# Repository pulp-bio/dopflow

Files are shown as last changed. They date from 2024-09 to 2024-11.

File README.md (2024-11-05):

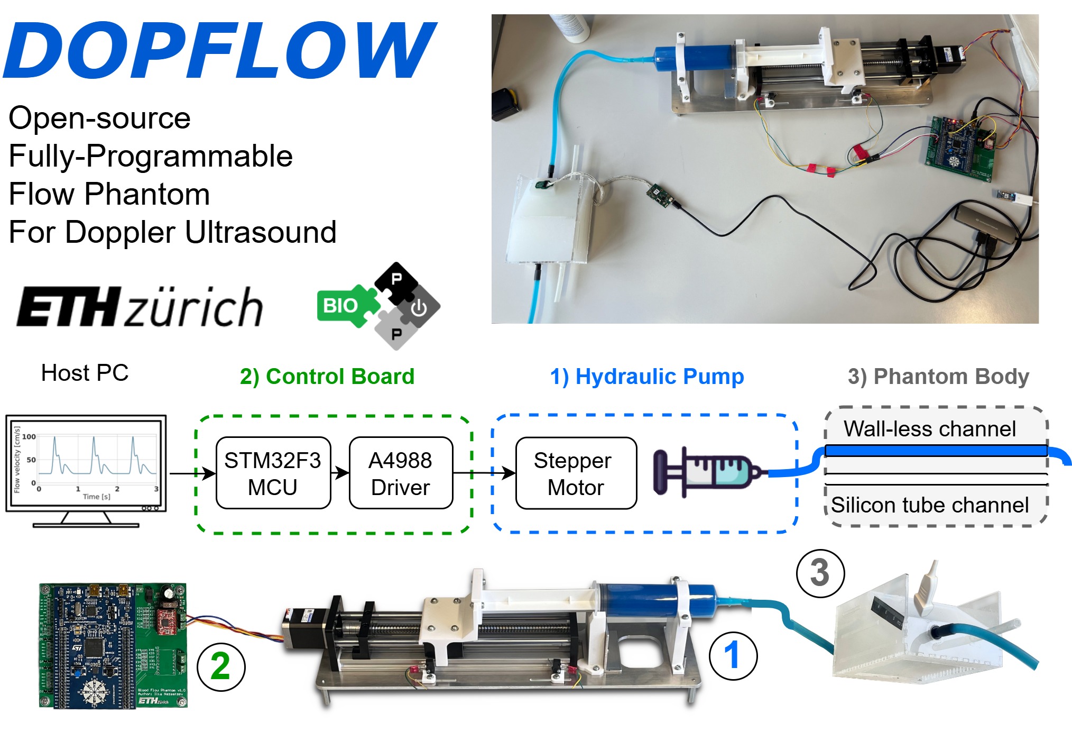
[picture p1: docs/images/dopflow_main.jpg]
DOPFLOW main


# DOPFLOW: 
## Open-Source Fully-Programmable Flow Phantom for Doppler Ultrasound
# Introduction

This repository contains the design files to reproduce the DOPFLOW system presented at IUS Joint Symposium 2024 [1].

DOPFLOW is an all-in-one Doppler Flow Phantom system that mimics the common carotid artery.
The platform has a modular design using off-the-shelf parts, including
- Custom syringe-based hydraulic pump, 
- Control printed circuit board, 
- Phantom body with both walled and wall-less channels,
- Graphical User Interface. 

The platform allows users to define pulsatile patterns, achieves maximum flow speeds over 1 meter per second and was validated with a commercial ultrasound Doppler machine (SONIX RP). These capabilities, plus the system's low cost (< 300 $) and open-source design, make DOPFLOW a promising research tool for developing new Doppler ultrasound technologies.

# Structure of the repository
This repository has the following folders:
- `control_board`, containing the source files to reproduce the control board.
- `hydraulic pump`, containing the source files to reproduce the hydraulic pump.
- `phantom`, containing the source files to reproduce the phantom structure, mimicking the common carotid artery and surrounding tissue.
- `software`, containing the source files for the graphical user interface (GUI) to control the motor.
- `docs`, containing the project documentation (e.g., images of the device, user manual, ...)

# Documentation 

The comprehensive [DOPFLOW User Manual](docs/dopflow_user_manual.pdf) located in the `docs/` folder, provides complete information on the DOPFLOW system, from assembly instructions to a detailed GUI overview. It’s designed to make the platform accessible and user-friendly for all, regardless of technical background.

# How to reproduce?

In a nutshell, to set up your own instance of DOPFLOW, follow these steps:

1. *Fabricate and assemble the hardware*<br>
   First, fabricate the phantom body and the hydraulic pump, then assemble and program the control board using instructions from the chapter 2 of the  [User Manual](docs/dopflow_user_manual.pdf) 

2. *Python dependencies installation on the host PC*<br>
   Follow the instructions in the `./software/` folder to install the dependencies.

# Usage

Please refer to chapter 3 of the [DOPFLOW User Manual](docs/dopflow_user_manual.pdf) for detailed information.

1. *Connect and power the control board*<br>
   Connect the PC to the control board, attach the hydraulic pump to the control board (connecting both the motor and limit switches), and power the control board using a 12 V, 2A lab power supply.

2. *Connect the phantom to the hydraulic pump*<br>
   Use a silicone hydraulic line to connect the phantom to the syringe pump.

3. *Run the graphical user interface (GUI)*<br>
   Launch the GUI, and use the controls to move the syringe and fill the phantom with the blood-mimicking fluid.

4. *Place the ultrasound transducer and perform measurements*<br>
   Position the ultrasound transducer on the phantom, run the custom pulse profile, and proceed with the measurements.

# Citation

[1] - Vostrikov Sergei et. al, "Open-Source Fully-Programmable Flow Phantom for Doppler Ultrasound." 2024 IEEE Ultrasonics, Ferroelectrics, and Frequency Control Joint Symposium (UFFC-JS). IEEE, 2024.

If you would like to reference the project, please cite the following paper:

```
@inproceedings{vostrikov2022opensource,
  title={Open-Source Fully-Programmable Flow Phantom for Doppler Ultrasound},
  author={Vostrikov, Sergei and Tille, Josquin and Nazemtsev, Ilia and Benini, Luca and Cossettini, Andrea},
  booktitle={2024 IEEE Ultrasonics, Ferroelectrics, and Frequency Control Joint Symposium (UFFC-JS)},
  pages={1--4},
  year={2024},
  organization={IEEE}
}
```

# Authors

The DOPFLOW system was developed at the [Integrated Systems Laboratory (IIS)](https://iis.ee.ethz.ch/) at ETH Zurich by:
- [Sergei Vostrikov](https://scholar.google.com/citations?user=a0KNUooAAAAJ&hl=en) (System design, Technical Supervision, Open-Sourcing)
- [Josquin Tille](https://www.linkedin.com/in/josquin-tille-829a341a7/) (Mechanical/PCB/Software design of the final prototype)
- [Nazemtsev Ilia](https://www.linkedin.com/in/ilia-nazemtsev/) (Mechanical/PCB/Software design of the initial prototype, Materials/Components selection)
- [Luca Benini](https://scholar.google.com/citations?hl=en&user=8riq3sYAAAAJ) (Supervision, Conceptualization)
- [Andrea Cossettini](https://scholar.google.com/citations?user=d8O91jIAAAAJ&hl=en) (Supervision, Project administration)

# License
Please see the [LICENSE_README.md](./LICENSE_README.md) for a summary of license information.

## Limitation of Liability
In no event and under no legal theory, whether in tort (including negligence), contract, or otherwise, unless required by applicable law (such as deliberate and grossly negligent acts) or agreed to in writing, shall any Contributor be liable to You for damages, including any direct, indirect, special, incidental, or consequential damages of any character arising as a result of this License or out of the use or inability to use the Work (including but not limited to damages for loss of goodwill, work stoppage, computer failure or malfunction, or any and all other commercial damages or losses), even if such Contributor has been advised of the possibility of such damages.

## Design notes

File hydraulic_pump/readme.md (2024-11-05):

# Assembly of the Hydraulic Pump
In this folder, you can find the files necessary to build the syringe based hydraulic pump.

For a step-by-step assembly instruction, please refer to the User manual located in `/docs/` folder and to the assembly video `assembly_animation.mp4` located in `/hydraulic_pump/`.

## Machined part
- `Ground_plate Drawing v4.pdf`, `Ground_plate.step`, are the plans to build the ground plate on which the component are mounted. It is made from a 5mm thick 500mm x 135mm aluminum plate. The pdf techincal drawing includes the specifications for the tolerances and threads

## 3D Printed parts
The 3D printed parts are printed with PLA using FDM printing
- `Barrel_holder_1.stl`, `Syringe_holder_2.stl` and `cap_1.stl` are the three element connecting the the syringe to the base plate
- `plunger_puller_4.stl` and `plunger_pusher_2.stl` are connecting the plunger to the CNC rail.

- `lim_sitch_holder_3.stl` needs to be printed 2x, once normaly and once **mirrored** along the xz plan

- `spacer_raiL1.stl` can be inserted between the end plate on the motor side of the CNC rail and the aluminum extrusion of the CNC rail if the motor's shaft is too long and extends into the ballscrew mechanism. 

## Off the shelf parts to order

Off the shelf parts have to be order online. More iformation about the products as well as links to the providers are found in the Bill of material: `pump_BOM.xlsx`
### Coupling CNC rail with step motor
The CNC motor comes with a coupling however it does not fit the step motor shaft's diamter. You should order a motor coupling with diameter 6mm and 8mm. 

## Assembly visual description
For assembly refer to the assembly video: https://youtu.be/GyMb5HX_3No.

The image below maps the names of the files to the components. 

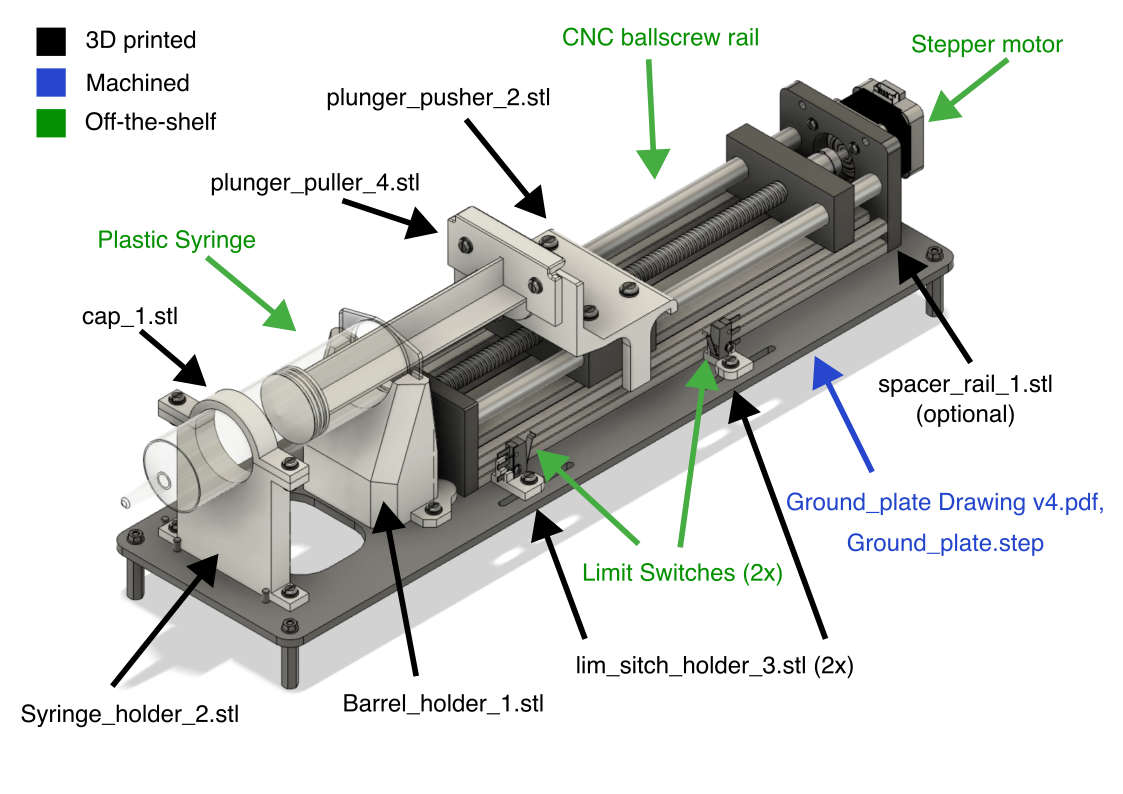
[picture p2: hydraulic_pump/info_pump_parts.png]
Hydraulic pump schematic


## Screws and Dowel pins 
Dowel pins for alignement: **ISO 2338 - ⌀4 h6 x 10mm** (7x)

Screws and washer:
- **Ground plate to CNC rail**: Stainless Steel Pan Head Slotted Screws **M6 x 15mm** + M6 washer (4x)
- **Plunger pusher to CNC rail**: Stainless Steel Pan Head Slotted Screws **M5 x 15mm** + M5 washer (4x)
- **Step motor to CNC rail**: Stainless Steel Pan Head Slotted Screws **M3 x 12mm** + M3 washer (4x)
- **Limit switch to lim stich holder**: Stainless Steel Pan Head Slotted Screws **M2 x 15mm** + M2 hex nut (2x) and M2 washer (4x)
- **All other Screws**: Stainless Steel Pan Head Slotted Screws **M4 x 15mm** + M4 hex nut (10x)  and M4 washer (20x)

- **4 support legs**: spacer, hex, M4 X 12mm

## Adjustment of the Limit Switches
The swithes can be mounted on the oblong holes on the side of the ground plate. To find the right position, 
- Start by mounting the Switches onto the holder. 
- Turn ballscrew mannualy until the syringe is almost empty (before the plunger touches the bottom of the barrel).
- Adjust the position of the holder so that the switch bumps into the plunger pusher and closes the circuit. 
- Turn ballscrew mannualy until the syringe is almost full (before the syringe breaks open).
- Adjust the position of the second holder so that the switch bumps into the plunger pusher and closes the circuit.

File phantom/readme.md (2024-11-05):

# Phantom's body fabrication

This directory contains the necessary instructions and files for fabricating a phantom body, including materials and steps for creating both walled and wall-less channels.

For a step-by-step manufacturing and assembly instructions, please refer to the User manual located in `/docs/` folder of the root directory of the repository.

## Summary of the Fabrication Steps

1. **Acrylic Frame Laser Cutting**
    - Laser cut the file `AcrilicBoxV4.svg` in acrylic and assemble the box using [acrifix glue](https://link-url-here.org).
    - Laser cut the `support_consturction_blocks.svg` using wither plywood or acrylic. 

2. **Prepare the Mold**
   - Insert a **silicone tube** (6 mm inner diameter) into pre-arranged holes in the frame. You can also add a metalic rod int the tube to ensure it will stay straight.
   - Place a **steel rod** (6 mm diameter) for the wall-less channel. TIP: coat the steel rod with petrolum jelly for easier removal
   - Seal all the open holes with transparent tape. You can print `phantom_hole_lid.stl`to cover the holes of the wall-less channel.
   - Place the frame onto the suport blocs

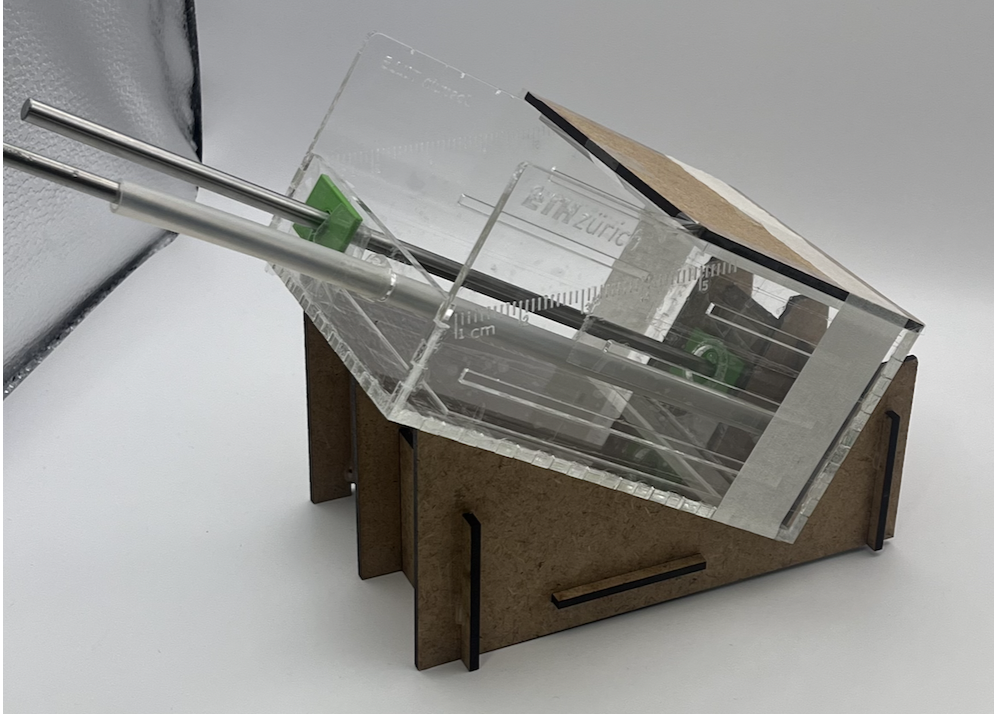
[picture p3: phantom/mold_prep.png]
Mold preparation


3. **Filling with Tissue-Mimicking Material**
   - Prepare a tissue-mimicking silicone rubber material (EcoFlex 30, Smooth-On, USA).
   - Mix part A and B with a 1:1 ratio.
   - Degas the EcoFlex silicone for **60 seconds** under a medium vacuum level (**15-20 mbar**) to remove any air bubbles.
   - After degassing, pour the silicone into the acrylic frame.
   - Allow the silicone to cure for **4 hours**.

4. **Removing the Sacrificial parts**
   - Once cured, carefully remove the steel rod from the phantom, leaving behind a **cylindrical wall-less channel**.
   - Remove all other sacrificial parts.
   - Insert the inlet to conect the wall-less channel to a conveyor silicon tube.

---

This process results in a phantom body with both walled and wall-less channels.
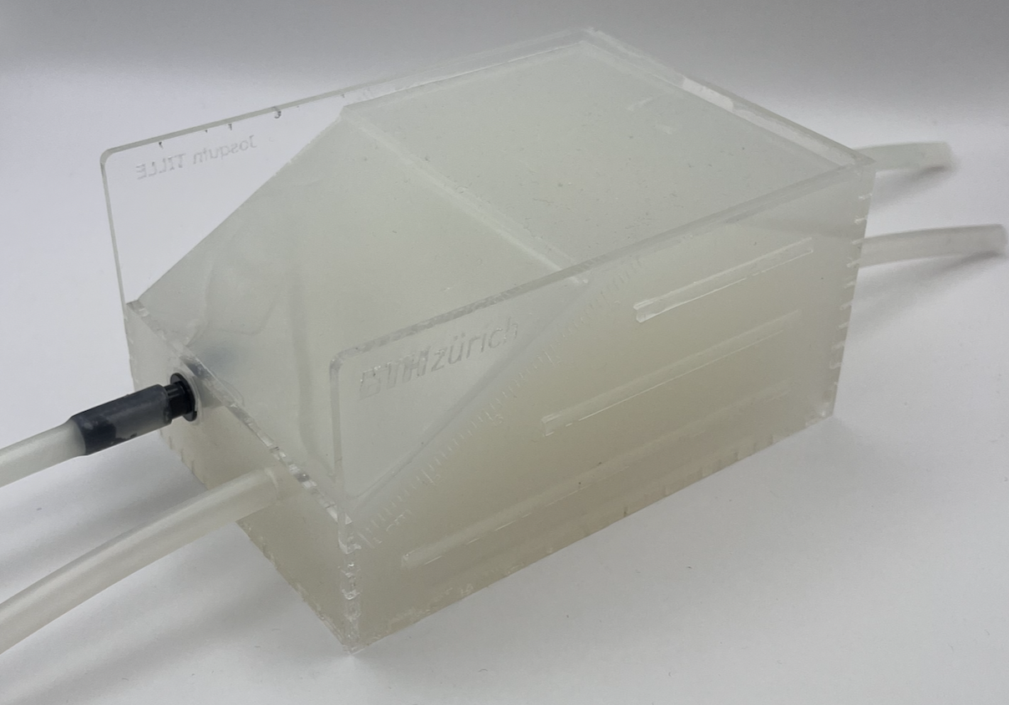
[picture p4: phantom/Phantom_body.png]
Mold final


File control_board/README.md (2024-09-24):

# Control board printed circuit board and firmware
This directory contains the following source files for the control board:
- Printed circuit board design files (`hw` folder)
- STM32 firmware (`fw` folder)

Please refer to the particular folder for license information.

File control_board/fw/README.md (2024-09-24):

# Flashing the firmware to the control board

### 1. Download STM32CubeIDE
Download and install the latest version **1.12.1** of STM32CubeIDE from the [ ST website](https://www.st.com/en/development-tools/stm32cubeide.html#get-software).

### 2. Create a new project
- In STM32CubeIDE go to File > New > STM32 Project from an Existing STM32CubeMX Configuration File (.ioc).<br>
- Select the file in `phantom_control/phantom_control.ioc` and press Finish.<br>
- Next, overwrite the files in the folders `Core/*` and `USB_DEVICE/*` (USB interface files) from this repository. 
For this, drag and drop both folders to the newly created project located in `C:\Users\USERNAME\STM32CubeIDE\workspace_1.12.1\phantom_control`. Select Copy files and folders, click OK and then Overwrite All.<br>
### 3. Build and Flash the project
- You can now build the project, and flash it to the STM32F3DISCOVERY board plugged into the control PCB. <br>
- To control the motor and run a custon flow profile, use the GUI in `./software` folder of the repository.

# Authors
- The initial control board firmware was developed by [Nazemtsev Ilia](https://www.linkedin.com/in/ilia-nazemtsev/). Subsequent updates and major improvements were implemented by [Josquin Tille](https://www.linkedin.com/in/josquin-tille-829a341a7/).

# License
The files in the `control_board/fw/` directory contains third-party sources that come with their own licenses. See the respective folders and source files' headers for the licenses used.
The code developed at IIS comes under Apache License 2.0 (`Apache-2.0`) (see `control_board/LICENSE`).

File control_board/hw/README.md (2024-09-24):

# Control board PCB design files
This directory contains the design files for the control printed circuit board (PCB) of the DOPFLOW project.
Inside the `altium_project` folder you can find the Altium CAD design files and generated schematics (.pdf), bill of materials (.xlsx) and fabrictaion files located in the `docs` folder.

To reproduce the project please use the fabrication files located in `altium_project/docs/fabrication_files` and send them directly to your PCB manufacturer.

# License
The PCB design files are licensed under Solderpad v0.51 (`SHL-0.51`) license. Please, check the `hw/LICENSE` file for details

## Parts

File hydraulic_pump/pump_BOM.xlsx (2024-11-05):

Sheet: Mechanical
Mechanical and electrical parts for the Hydraulic Pump
Description | Manufacture | Manufacture Part Number | Supplier | Link | Supplier Part Number | Supplier Unit Price | Quantity
CNC ballscrew rail 200mm effective stroke | CNCCANEN | SFU1204 | aliexpress | https://de.aliexpress.com/item/1005001626958180.html?mp=1 | 200mm Effective Stroke CNC Linear Guide Stage Rail Motion GGP SFU1204 Ballscrew Slide Table 3D Printer XYZ | CHF 47.24 | 1
2-Phase Step Motor, Single Shaft, 42mm, Bipolar,1.8 deg, 24 VDC, 1 A/phase, NEMA 17, 510 g | SANMOTION | SF2424-10B41 | SANMOTION | https://www.mouser.ch/ProductDetail/SANMOTION/SF2424-10B41?qs=l4Gc20tDgJL8XFkD8zVbZQ%3D%3D | SF2424-10B41 | CHF 27.54 | 1
Flexible Motor Shaft Coupling 6mm to 8mm | WHOOPEE | D19l25 | aliexpress | https://de.aliexpress.com/item/1005006513457969.html? | D19l25 6x8 | CHF 1.40 | 1
Dowel pins (ISO 2338 ∅4 h6) | GooBetter | Diameter 4 mm | aliexpress | https://de.aliexpress.com/item/1005007581698118.html | Diameter 4 mm | CHF 1.01 | 1 package (7 pins minimum)
Limit Switches | Omron Electronics Inc-EMC Div | SS-3GL13PT | DigiKey | https://www.digikey.ch/en/products/detail/omron-electronics-inc-emc-div/SS-3GL13PT/664729 | SW768-ND | CHF 1.28 | 2
Plastic Syringe, inner diameter is 40 mm, plunge length is 15.5 cm | Changlesu | B07GZKR2GW | Amazon | https://www.amazon.de/-/en/Changlesu-Reusable-Syringes-Aquariums-Agriculture/dp/B07GZKR2GW | B07GZKR2GW | CHF 10.99 | 1
Screws and washers |  |  |  |  |  |  | M3 x 12 > 4 pieces, M4 x 15 > 10 pieces, M3 x 12 > 4 pieces, M5 x 15 > 4 pieces, M6 x 15 > 4 pieces
Steel Hex spacer (M4x12) |  |  |  |  |  |  | 4

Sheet: Manufactured parts
Part name | Material | Manufacturing methode | Manufacturing time | number of unit | estimated raw material cost per unit
Base Plate | Aluminium | Machining | ~2h | 1 | CHF 0.00
Syringe Flange holder | PLA | FDM printing | 7h14 | 1 | CHF 1.17
Syringe barrel holder | PLA | FDM printing | 5h40 | 1 | CHF 0.88
Syringe barrel holder cap | PLA | FDM printing | 1h30 | 1 | CHF 0.18
Limmiter switch holder | PLA | FDM printing | 0h25 | 2 | CHF 0.00
Plunger pusher | PLA | FDM printing | 8h5 | 1 | CHF 1.20
Plunger puller | PLA | FDM printing | 1h30 | 1 | CHF 0.26
Acrylic Sheet | acrylic | Laser cutting | 10min | 1 | CHF 25.00
Total |  |  |  |  | CHF 28.69

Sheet: TMM_VMM
Description | Supplier | Link | Supplier Part Number | Supplier Unit Price | Quantity
6 mm steel rod to form wall-less phantom | Amazon | https://www.amazon.de/-/en/gp/product/B07LG7VFY5/ref=ewc_pr_img_1?smid=AQ1IBDB6G2RRD&psc=1 | B07LG7VFY5 | CHF 6.02 | 1
Silicon tubing inner/outer diameter: 6/8 mm | schlauch-profi.de | https://www.schlauch-profi.de/silikonschlauch-fda-bfr-konform-lebensmittel-naturfarben-158?number=1000396-8 | 1000396-8 | CHF 3.80 | 2 m
PVC hose 10/14 mm | alba-therm | https://www.alba-therm.ch/de/PVCSchlauch_10x2_50m.a239.2.html | 10022487 | CHF 5.95 | 4 m
Verbindungstüllen reduktionsstück GRS 10/6 mm | alba-therm | https://www.alba-therm.ch/de/Verbindungsstueck_GRS10_6MM.a6950.2.html | 10316140 | CHF 5.35 | 8
ECO-FLEX™ 0030/1 | kaupo.de | https://www.kaupo.de/shop/en/SILICONE-RUBBER-Platinum-Cure/ECOFLEX-SERIES/Ecoflex-00-30/ECO-FLEX-0030-1-Silicone-Rubber.html | 09301-005-000041 | 38.81 € | 1
Doppler Fluid | bachmann-lehrmittel.ch | https://bachmann-lehrmittel.ch/GAMPT-Doppler-Fluessigkeit-Doppler-Fluid/GP50140 | GP50140 | CHF 86.40 | 1
Total |  |  |  |  | 205.43

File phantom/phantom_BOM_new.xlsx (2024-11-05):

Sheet: Mechanical
Mechanical parts for the Phantom Body
Description | Manufacture | Manufacture Part Number | Supplier | Link | Supplier Unit Price | Quantity
Acrylic sheet (3 mm thickness) |  |  |  |  |  | 1 sheet (300x300 mm)
Plywood sheet (3 mm thickness) |  |  |  |  |  | 1 sheet (300x220 mm)
Acrifix glue | Acrylite | - | Modulor | https://www.modulor.de/en/acrifix-192-acrylic-glue.html | CHF 11,75 | 1
Silicone tube (6 mm inner, 8 mm outer diameter) | Hans Kraeft GmbH & Co.KG | - | Schlauch-Prof | https://www.schlauch-profi.de/Silikonschlauch-FDA-BfR-konform-Lebensmittel-naturfarben/1000391-2M | CHF 3,47 | 2
Steel rod (6 mm diameter, > 20 cm)
Steel rod (5 mm diameter, > 20 cm)
EcoFlex 30 | Smooth On | ECO-FLEX™ 0030/1 | KauPo Plankenhorn e.K. | https://www.kaupo.de/shop/en/SILICONE-RUBBER-Platinum-Cure/ECOFLEX-SERIES/Ecoflex-00-30/ECO-FLEX-0030-1-Silicone-Rubber.html | CHF 36,47 | 1
Blood Mimicking Fluid | GAMPT | GAMPT Doppler Flüssigkeit / Doppler Fluid | Bachmann Lehrmittel AG | https://bachmann-lehrmittel.ch/GAMPT-Doppler-Fluessigkeit-Doppler-Fluid/GP50140 | CHF 86,5 | 1
Plastic hose connector (8 mm to 6 mm) |  |  |  |  |  | 5
Petroleum jelly |  |  |  |  |  | 10 ml

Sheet: Manufactured parts
Part name | Material | Manufacturing methode | Manufacturing time | number of unit | estimated raw material cost per unit
Base Plate | Aluminium | Machining | ~2h | 1 | CHF 0.00
Syringe Flange holder | PLA | FDM printing | 7h14 | 1 | CHF 1.17
Syringe barrel holder | PLA | FDM printing | 5h40 | 1 | CHF 0.88
Syringe barrel holder cap | PLA | FDM printing | 1h30 | 1 | CHF 0.18
Limmiter switch holder | PLA | FDM printing | 0h25 | 2 | CHF 0.00
Plunger pusher | PLA | FDM printing | 8h5 | 1 | CHF 1.20
Plunger puller | PLA | FDM printing | 1h30 | 1 | CHF 0.26
Acrylic Sheet | acrylic | Laser cutting | 10min | 1 | CHF 25.00
Total |  |  |  |  | CHF 28.69

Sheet: TMM_VMM
Description | Supplier | Link | Supplier Part Number | Supplier Unit Price | Quantity
6 mm steel rod to form wall-less phantom | Amazon | https://www.amazon.de/-/en/gp/product/B07LG7VFY5/ref=ewc_pr_img_1?smid=AQ1IBDB6G2RRD&psc=1 | B07LG7VFY5 | CHF 6.02 | 1
Silicon tubing inner/outer diameter: 6/8 mm | schlauch-profi.de | https://www.schlauch-profi.de/silikonschlauch-fda-bfr-konform-lebensmittel-naturfarben-158?number=1000396-8 | 1000396-8 | CHF 3.80 | 2 m
PVC hose 10/14 mm | alba-therm | https://www.alba-therm.ch/de/PVCSchlauch_10x2_50m.a239.2.html | 10022487 | CHF 5.95 | 4 m
Verbindungstüllen reduktionsstück GRS 10/6 mm | alba-therm | https://www.alba-therm.ch/de/Verbindungsstueck_GRS10_6MM.a6950.2.html | 10316140 | CHF 5.35 | 8
ECO-FLEX™ 0030/1 | kaupo.de | https://www.kaupo.de/shop/en/SILICONE-RUBBER-Platinum-Cure/ECOFLEX-SERIES/Ecoflex-00-30/ECO-FLEX-0030-1-Silicone-Rubber.html | 09301-005-000041 | 38.81 € | 1
Doppler Fluid | bachmann-lehrmittel.ch | https://bachmann-lehrmittel.ch/GAMPT-Doppler-Fluessigkeit-Doppler-Fluid/GP50140 | GP50140 | CHF 86.40 | 1
Total |  |  |  |  | 205.43

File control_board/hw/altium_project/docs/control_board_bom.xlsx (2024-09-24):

Designator | Description | Comment | Quantity
A2 |  | 831-87-032-10-001101 | 1
C1 | Aluminum Electrolytic Capacitors (Radial Lead Type) 330uF ±20% 35V | 330uF | 1
C2, C3, C4 | Cap Ceramic 100nF 50V X7R ±10% SMD 1206 +125°C Embossed T/R | 100nF | 3
D1, D2, D3, D4, D5, D6, D7, D8 | DIODE ARRAY GP 100V 215MA SOT23 | BAV99,215 | 8
F1 | FUSE AUTO 5A 32VDC BLADE MINI | 0297005.WXNV | 1
FB1 | Ferrite Bead, 1806, 60Ω @ 100MHz, 0.009Ω, 6A | BLM41PG600SN1L | 1
J1, J2, J3, J4, J6 | Male Header, Pitch 2.54 mm, 1 x 2 Position, Height 9 mm, Tail Length 3.5 mm | 1725656 | 5
J5 | DC Power Jack Connector Low Profile WR-DC, Male, Right Angled, THT, 2 A, 12 V | 694101308002 | 1
M6 | Spacer M3 - 38mm | Spacer M3 | 1
M7 | Screw M3x8 Pan Head Phillips | Screw M3x8 | 1
R1, R2, R3 | Chip Resistor, 4.7 KOhm, +/- 1%, 0.125 W, -55 to 155 degC, 0805 (2012 Metric), RoHS, Tape and Reel | ERJ-6ENF4701V | 3
TB | STM32F303VCT6 Discovery STM32F3 ARMÂ® CortexÂ®-M4 MCU 32-Bit Embedded Evaluation Board | STM32F3DISCOVERY | 1
U1, U2 | Stepper motor controler; IC: A4988; 1A; Uin mot: 8Ã·35V | A4988_STEPPER_MOTOR_DRIVER_CARRIER | 2
X1 | 1 Positions Header, Unshrouded Connector Through Hole Gold or Gold, GXT™ | SPI1_NSS | 1
X2 | 1 Positions Header, Unshrouded Connector Through Hole Gold or Gold, GXT™ | SPI1_SCK | 1
X3 | 1 Positions Header, Unshrouded Connector Through Hole Gold or Gold, GXT™ | SPI1_MOSI | 1
X4 | 1 Positions Header, Unshrouded Connector Through Hole Gold or Gold, GXT™ | SPI1_MISO | 1
X5, X8, X11, X16, X21 | 1 Positions Header, Unshrouded Connector Through Hole Gold or Gold, GXT™ | GND | 5
X6 | 1 Positions Header, Unshrouded Connector Through Hole Gold or Gold, GXT™ | UART4_TX | 1
X7 | 1 Positions Header, Unshrouded Connector Through Hole Gold or Gold, GXT™ | UART4_RX | 1
X9 | 1 Positions Header, Unshrouded Connector Through Hole Gold or Gold, GXT™ | I2C1_SCL | 1
X10 | 1 Positions Header, Unshrouded Connector Through Hole Gold or Gold, GXT™ | I2C1_SDA | 1
X12 | 1 Positions Header, Unshrouded Connector Through Hole Gold or Gold, GXT™ | PB11 | 1
X13 | 1 Positions Header, Unshrouded Connector Through Hole Gold or Gold, GXT™ | PB12 | 1
X14, X19 | 1 Positions Header, Unshrouded Connector Through Hole Gold or Gold, GXT™ | PB13 | 2
X15, X20 | 1 Positions Header, Unshrouded Connector Through Hole Gold or Gold, GXT™ | PB14 | 2
X17 | 1 Positions Header, Unshrouded Connector Through Hole Gold or Gold, GXT™ | PD12 | 1
X18 | 1 Positions Header, Unshrouded Connector Through Hole Gold or Gold, GXT™ | PD13 | 1
X22 | 1 Positions Header, Unshrouded Connector Through Hole Gold or Gold, GXT™ | PH3 | 1
X23 | 1 Positions Header, Unshrouded Connector Through Hole Gold or Gold, GXT™ | PH4 | 1
X24 | 1 Positions Header, Unshrouded Connector Through Hole Gold or Gold, GXT™ | PH5 | 1
X25 | 1 Positions Header, Unshrouded Connector Through Hole Gold or Gold, GXT™ | PH6 | 1
X26 | 1 Positions Header, Unshrouded Connector Through Hole Gold or Gold, GXT™ | PH7 | 1
X27 | 1 Positions Header, Unshrouded Connector Through Hole Gold or Gold, GXT™ | PH8 | 1
X28 | 1 Positions Header, Unshrouded Connector Through Hole Gold or Gold, GXT™ | PH9 | 1
X29 | 1 Positions Header, Unshrouded Connector Through Hole Gold or Gold, GXT™ | PH10 | 1
X30 | 1 Positions Header, Unshrouded Connector Through Hole Gold or Gold, GXT™ | PH11 | 1
X31 | 1 Positions Header, Unshrouded Connector Through Hole Gold or Gold, GXT™ | PH12 | 1
X32 | 1 Positions Header, Unshrouded Connector Through Hole Gold or Gold, GXT™ | PH1 | 1
X33 | 1 Positions Header, Unshrouded Connector Through Hole Gold or Gold, GXT™ | PH2 | 1
X34 | 1 Positions Header, Unshrouded Connector Through Hole Gold or Gold, GXT™ | PH13 | 1
X35 | 1 Positions Header, Unshrouded Connector Through Hole Gold or Gold, GXT™ | PH14 | 1
X36 | 1 Positions Header, Unshrouded Connector Through Hole Gold or Gold, GXT™ | PH15 | 1
X37 | 1 Positions Header, Unshrouded Connector Through Hole Gold or Gold, GXT™ | PH16 | 1
X38 | 1 Positions Header, Unshrouded Connector Through Hole Gold or Gold, GXT™ | PH17 | 1
X39 | 1 Positions Header, Unshrouded Connector Through Hole Gold or Gold, GXT™ | PH18 | 1
X40 | 1 Positions Header, Unshrouded Connector Through Hole Gold or Gold, GXT™ | PH19 | 1
X41 | 1 Positions Header, Unshrouded Connector Through Hole Gold or Gold, GXT™ | PH20 | 1
X42 | 1 Positions Header, Unshrouded Connector Through Hole Gold or Gold, GXT™ | PH21 | 1
X43 | 1 Positions Header, Unshrouded Connector Through Hole Gold or Gold, GXT™ | PH22 | 1
X44 | 1 Positions Header, Unshrouded Connector Through Hole Gold or Gold, GXT™ | PH23 | 1
X45 | 1 Positions Header, Unshrouded Connector Through Hole Gold or Gold, GXT™ | PH24 | 1
XF1 | Fuse Holder, 20 A, 500 V, -50 to 145 degC, 4-Pin THD, RoHS | 3568 | 1
. | STM32F303VCT6 Discovery Evaluation Board | STM32F3DISCOVERY | 1
. | Stepper motor controller; IC: A4988 | Pololu A4988 | 2

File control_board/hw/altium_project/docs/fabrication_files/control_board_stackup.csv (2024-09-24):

Board Layer Stack
Number | Name | Type | Manufacturer | Material | Process | Thickness (mm) | Weight (oz) | Dk | Df | Orientation | Copper Orientation | Pullback distance (mm) | Description | Color | Constructions | Solid (%) | Resin (%) | Frequency (GHz) | GlassTransTemp (°C)
 | Top Overlay | Overlay
 | Top Solder | Solder Mask | Altium Designer | SM-001 |  | 0.01 |  | 4 | 0.03 |  |  |  | Solder Mask | #FF008000 |  | 1 |  | 1 | 125
 | Top Surface Finish | Surface Finish |  | PbSn | HASL | 0.004 |  |  |  |  |  |  |  | #FFF2F2F2
1 | Top Layer | Signal | Altium Designer | CF-004 | ED | 0.035 | 1 |  |  | Top | Above |  | Copper Foil
 | Dielectric 1 | Prepreg | Altium Designer | PP-017 |  | 0.2104 |  | 4 | 0.02 |  |  |  |  |  | 2116 |  | 57 | 1 | 180
2 | Int1 (GND) | Plane | Altium Designer | CF-004 | ED | 0.035 | 1 |  |  |  | Above | 0.508 | Copper Foil
 | Dielectric 3 | Core | Altium Designer | Core-039 |  | 1.065 |  | 4.8 | 0.02 |  |  |  | FR4 |  | 4-7628 |  | 40 | 1 | 180
3 | Int 2 (PWR) | Plane | Altium Designer | CF-004 | ED | 0.035 | 1 |  |  |  | Below | 0.508 | Copper Foil
 | Dielectric 5 | Prepreg | Altium Designer | PP-017 |  | 0.2104 |  | 4 | 0.02 |  |  |  |  |  | 2116 |  | 57 | 1 | 180
4 | Bottom Layer | Signal | Altium Designer | CF-004 | ED | 0.035 | 1 |  |  | Bottom | Below |  | Copper Foil
 | Bottom Surface Finish | Surface Finish |  | PbSn | HASL | 0.004 |  |  |  |  |  |  |  | #FFF2F2F2
 | Bottom Solder | Solder Mask | Altium Designer | SM-001 |  | 0.01 |  | 4 | 0.03 |  |  |  | Solder Mask | #FF008000 |  | 1 |  | 1 | 125
 | Bottom Overlay | Overlay
No impedances
Via types
# | Name | Type | Layers | Stack
1 | Thru 1:4 | Thru | Top Layer-Bottom Layer | Board Layer Stack
No back drills

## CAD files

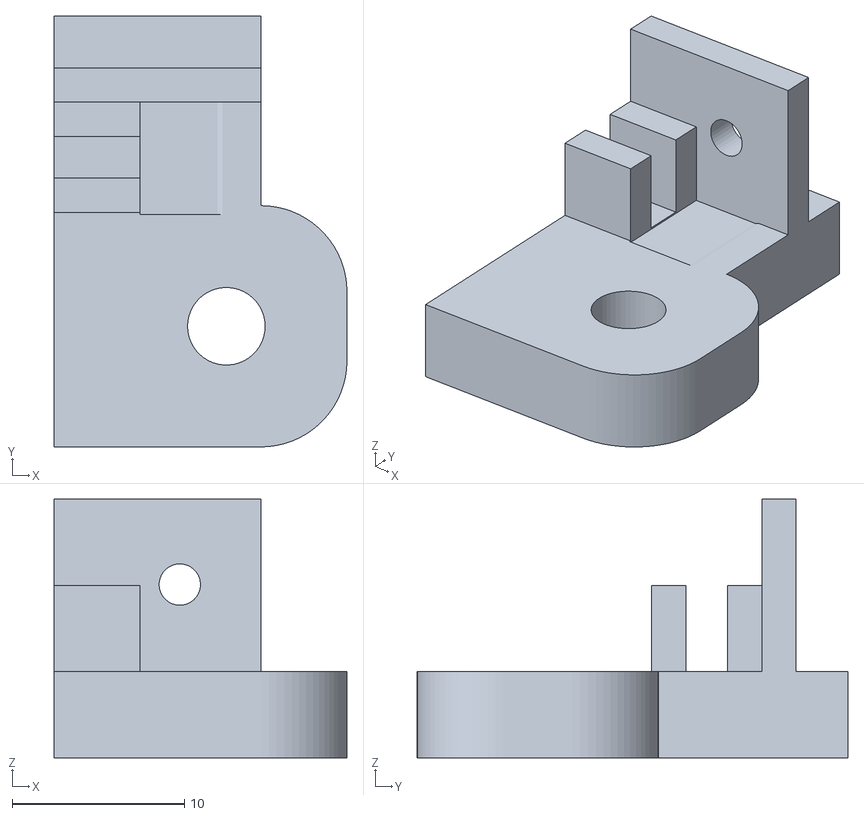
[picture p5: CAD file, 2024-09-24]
hydraulic_pump/3d_models/lim_sitch_holder_3.stl
17.0 x 25.0 x 15.0

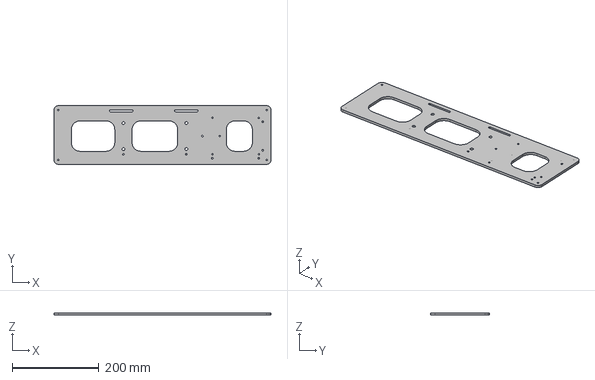
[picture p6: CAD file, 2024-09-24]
hydraulic_pump/Ground_plate.step
500.0 x 135.0 x 5.00 mm

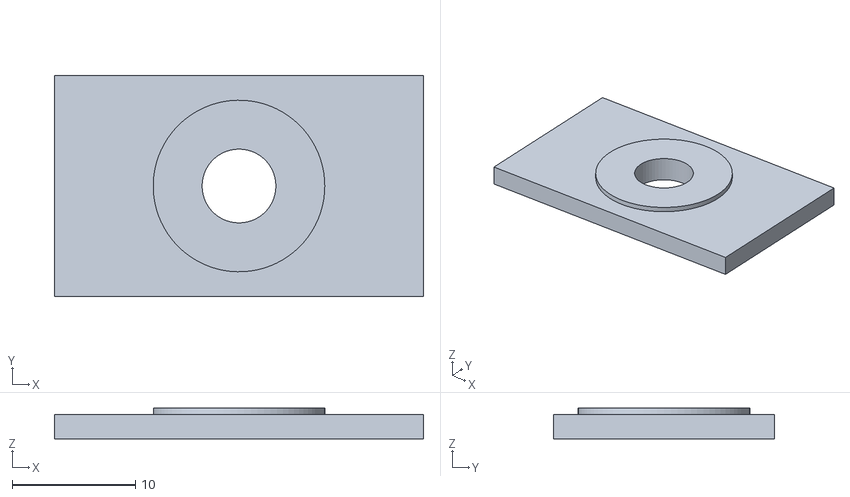
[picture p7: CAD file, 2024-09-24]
phantom/phantom_hole_lid.stl
30.0 x 18.0 x 2.50

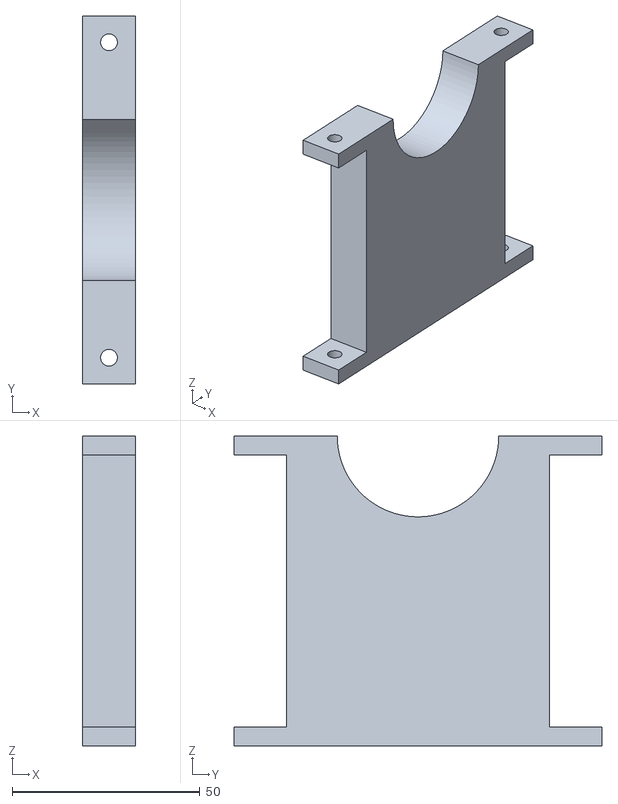
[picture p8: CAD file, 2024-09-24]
hydraulic_pump/3d_models/Syringe_holder_2.stl
14.0 x 98.0 x 82.5

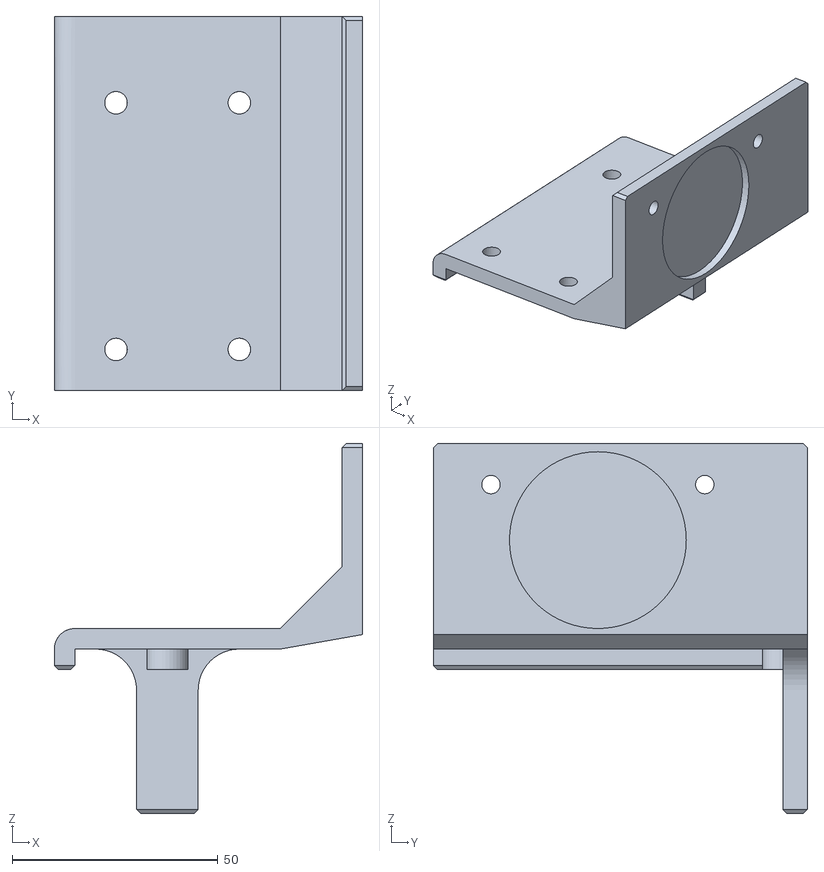
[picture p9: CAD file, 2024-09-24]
hydraulic_pump/3d_models/plunger_pusher_2.stl
75.0 x 91.0 x 90.0

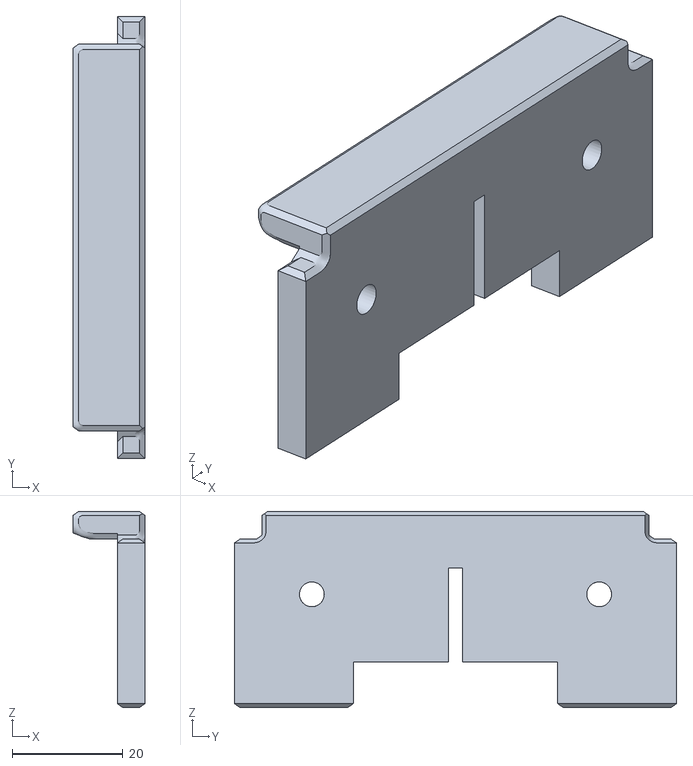
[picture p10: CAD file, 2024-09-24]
hydraulic_pump/3d_models/plunger_puller_4.stl
13.0 x 80.0 x 35.5

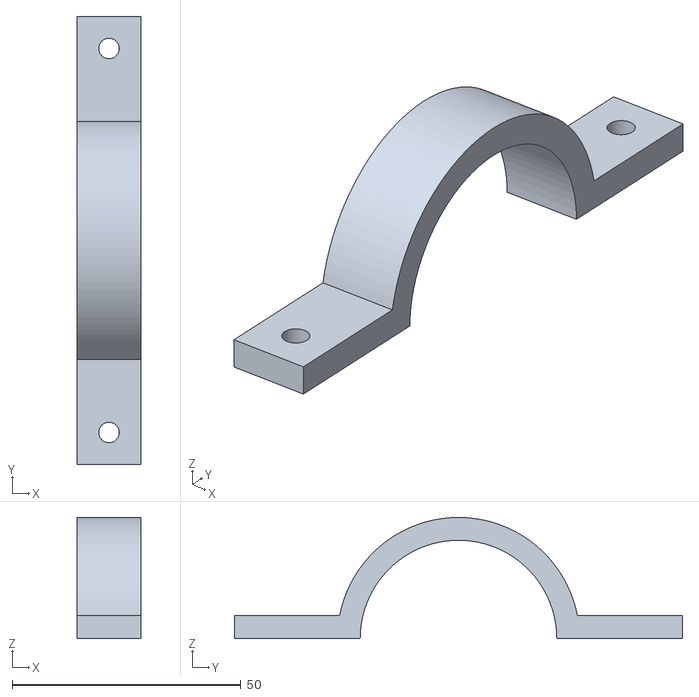
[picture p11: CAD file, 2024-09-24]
hydraulic_pump/3d_models/cap_1.stl
14.0 x 98.0 x 26.5

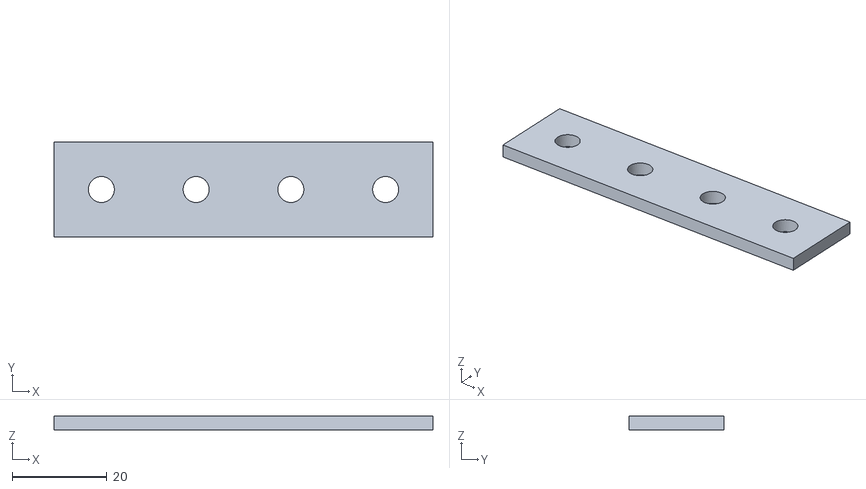
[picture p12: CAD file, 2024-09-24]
hydraulic_pump/3d_models/spacer_rail_1.stl
80.0 x 20.0 x 3.00

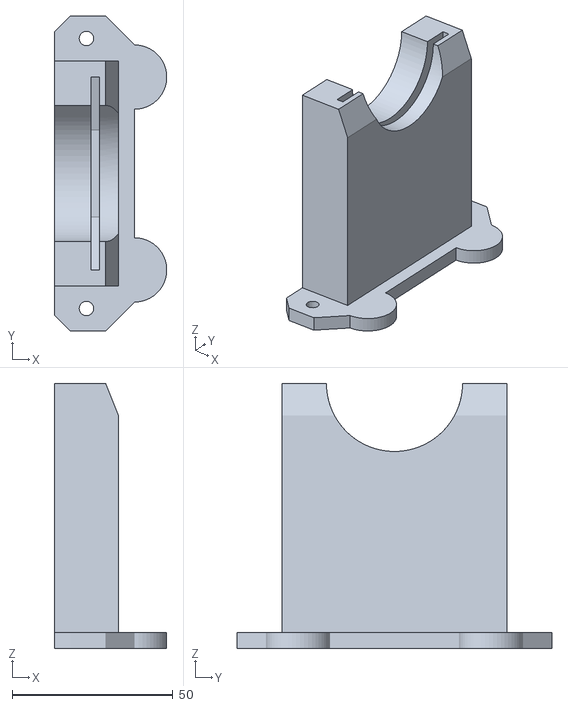
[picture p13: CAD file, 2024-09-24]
hydraulic_pump/3d_models/Barrel_holder_1.stl
35.0 x 98.0 x 82.5

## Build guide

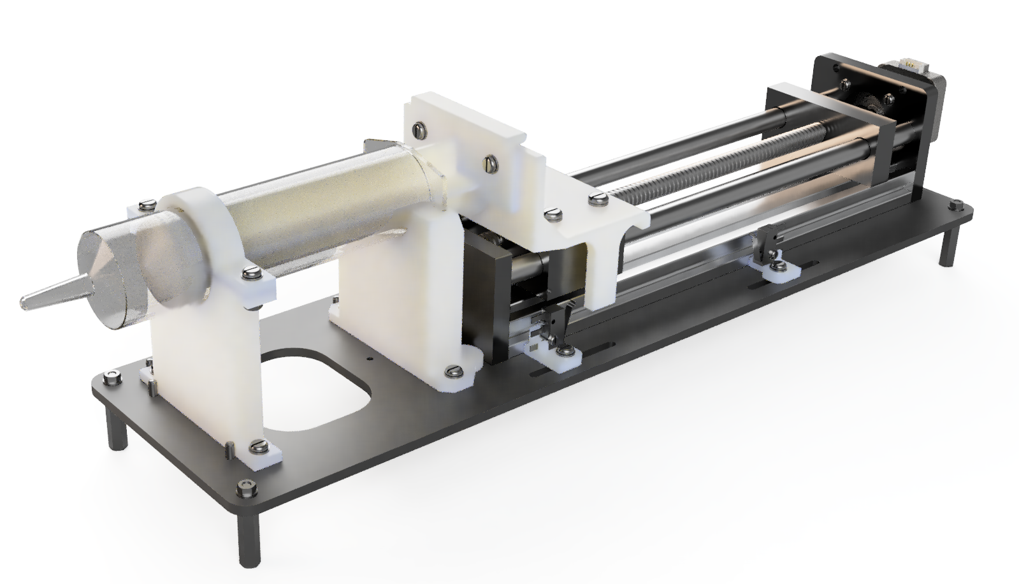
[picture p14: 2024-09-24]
docs/images/pump_assembly.png

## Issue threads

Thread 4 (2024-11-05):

### ISSUE TITLE
Control board - Reset of the A4988 driver

### ISSUE THREAD

**Issue by tillethz** [pulp-bio/dopflow#4]
The reset of the A4988 driver (D1_RESET line) is connected to pin 61 of the STM32 discovery board which is used by another sensor. this prevents the Driver from working. 
Please connect the D1_RESET line to the nrst pin of the STM32 discovery board (pin 4). That way you don't need a jumper wire from X29 to nrst and can add a simple jumper between X29 and X28.

<img width="392" alt="image" src="https://github.com/user-attachments/assets/767f19d6-944a-4f96-8294-dd2a643ee4ec">

**Comment by Sergio5714** [comment]
Fixed

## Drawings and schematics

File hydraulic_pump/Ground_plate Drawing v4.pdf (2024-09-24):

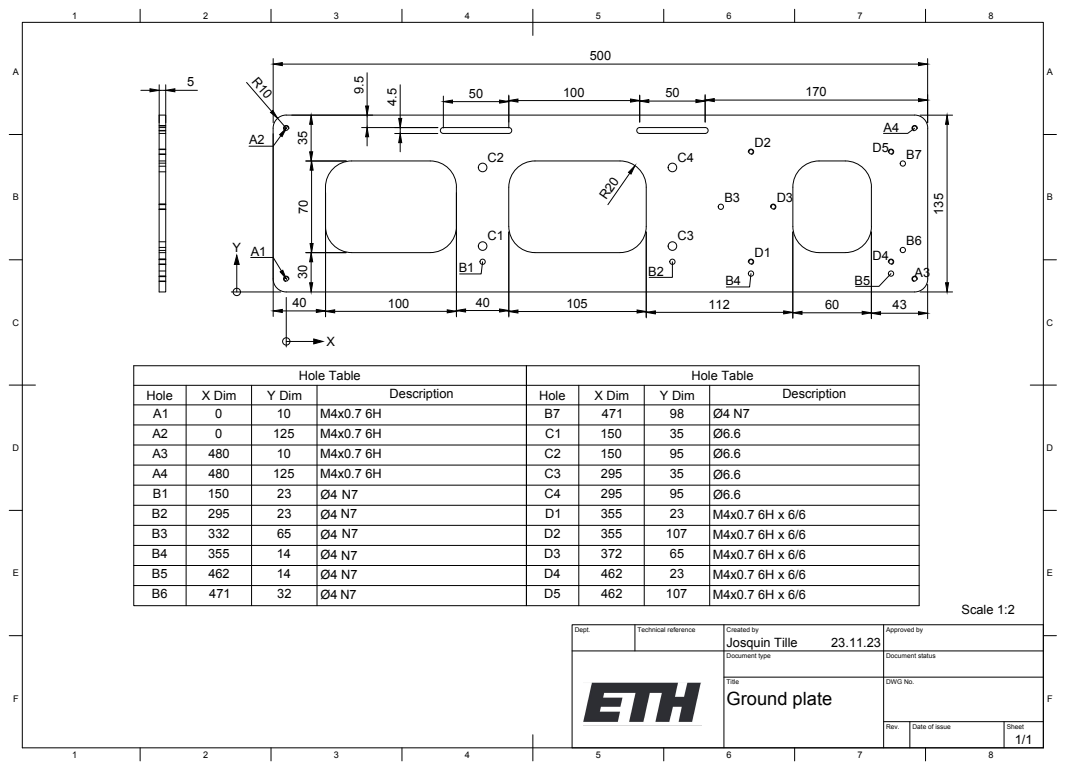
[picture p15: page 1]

Hole Table | Hole Table

Hole | X Dim | Y Dim | Description | Hole | X Dim | Y Dim | Description
A1 | 0 | 10 | M4x0.7 6H | B7 | 471 | 98 | Ø4 N7
A2 | 0 | 125 | M4x0.7 6H | C1 | 150 | 35 | Ø6.6
A3 | 480 | 10 | M4x0.7 6H | C2 | 150 | 95 | Ø6.6
A4 | 480 | 125 | M4x0.7 6H | C3 | 295 | 35 | Ø6.6
B1 | 150 | 23 | Ø4 N7 | C4 | 295 | 95 | Ø6.6
B2 | 295 | 23 | Ø4 N7 | D1 | 355 | 23 | M4x0.7 6H x 6/6
B3 | 332 | 65 | Ø4 N7 | D2 | 355 | 107 | M4x0.7 6H x 6/6
B4 | 355 | 14 | Ø4 N7 | D3 | 372 | 65 | M4x0.7 6H x 6/6
B5 | 462 | 14 | Ø4 | D4 | 462 | 23 | M4x0.7 6H x 6/6
B6 | 471 | 32 | Ø4 N7 | D5 | 462 | 107 | M4x0.7 6H x 6/6

Dept. | Technical reference | Created by Josquin Tille 23.11.23 | Approved by

Document type | Document status

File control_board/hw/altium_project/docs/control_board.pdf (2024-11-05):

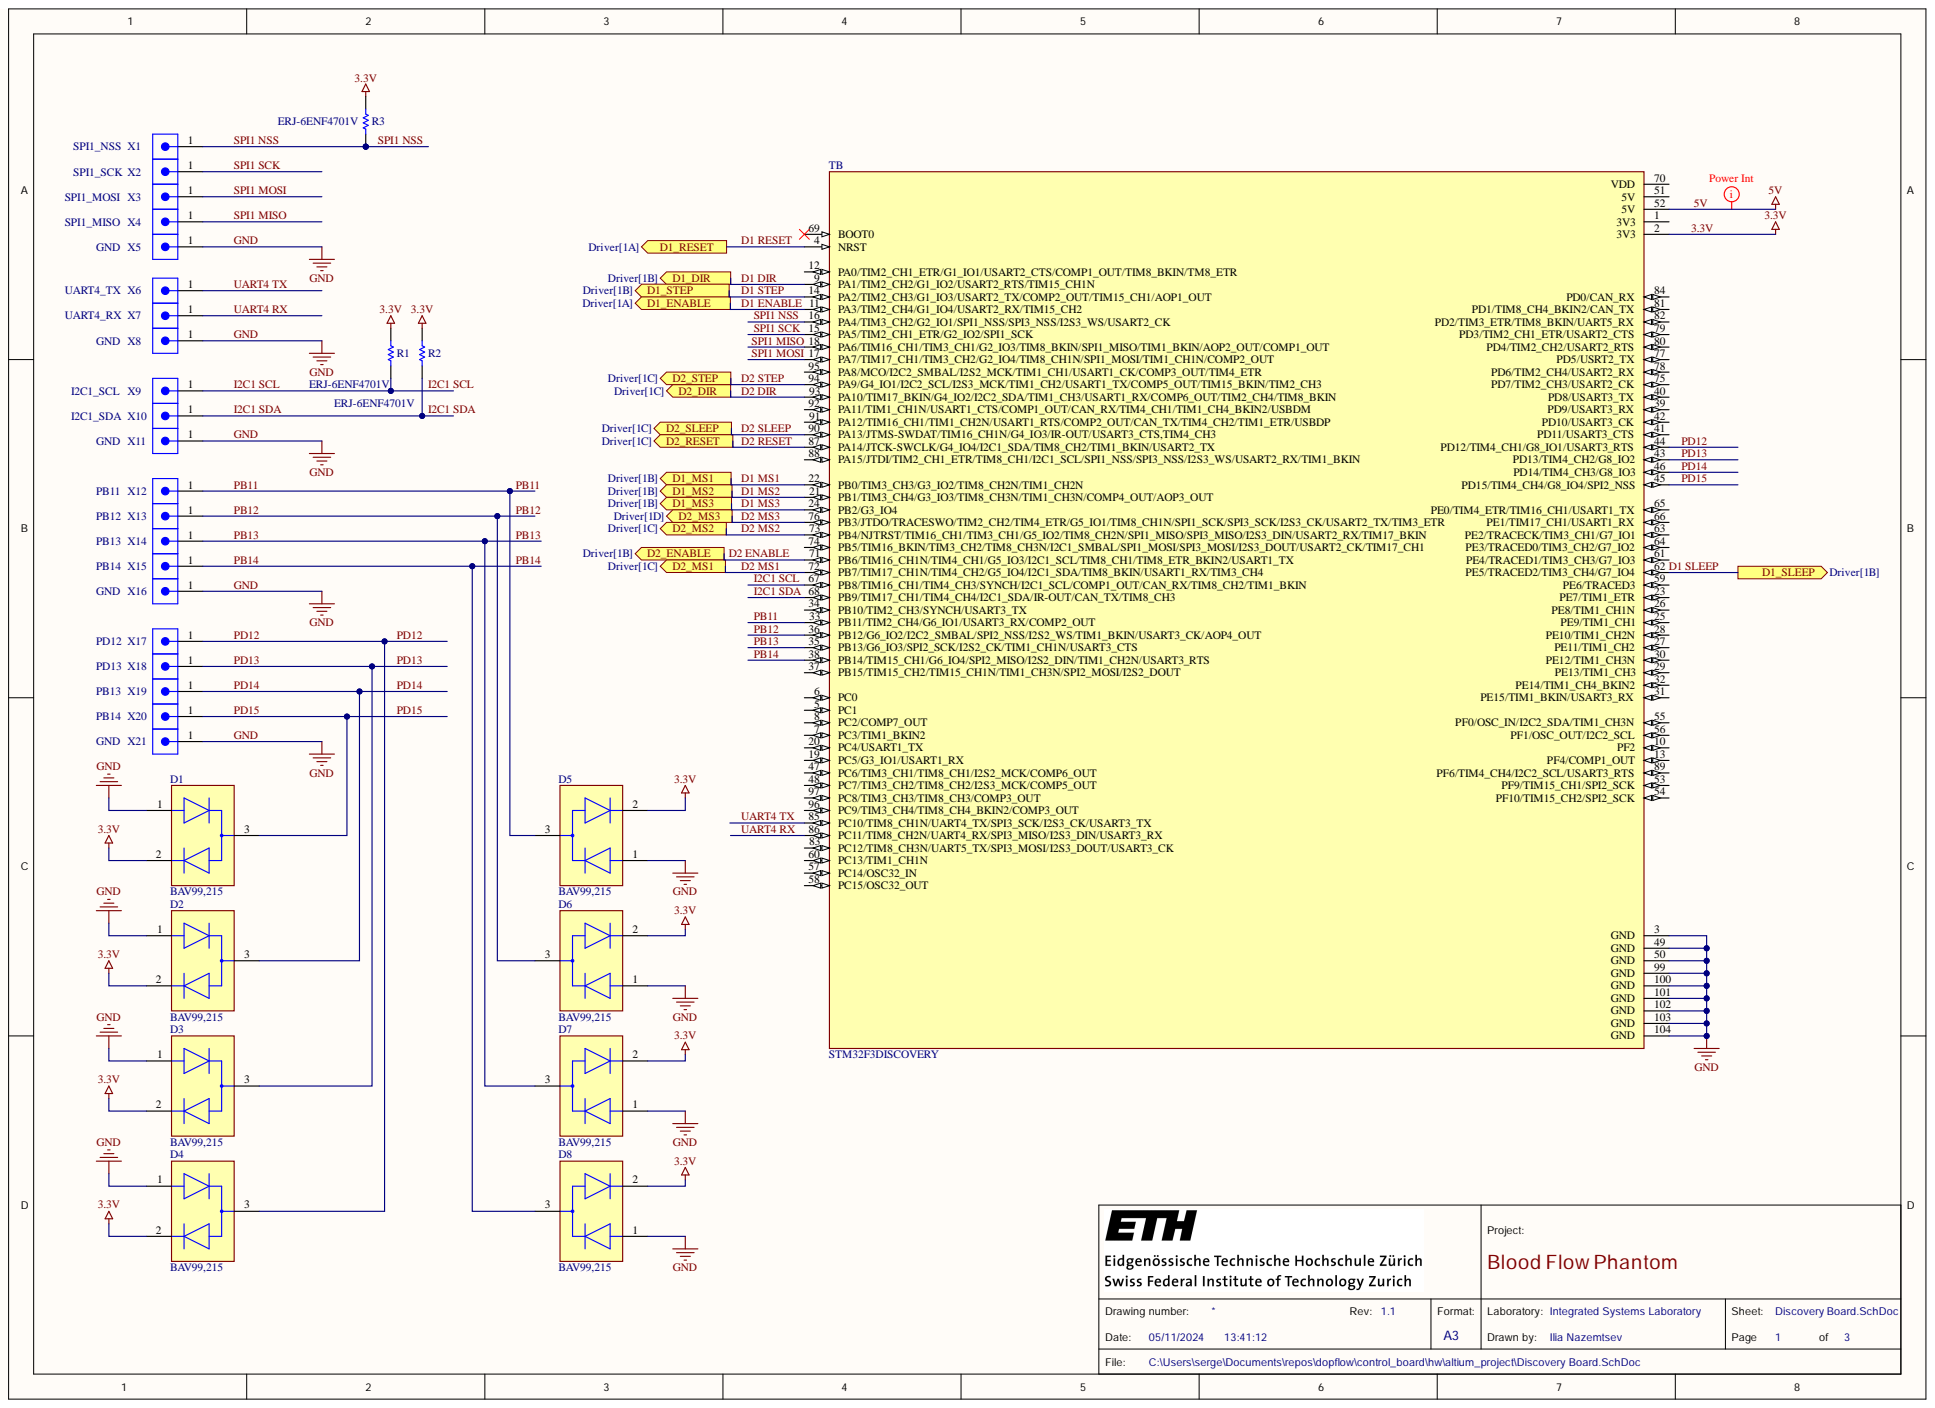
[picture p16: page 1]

3.3V GND GND GND GND

P roj e c t: B l o o d F l o w P h a n to m

ra wi n g n umb r: * R v . D a te 05/1 | F o rma t: A | L a b o ra to ry I n te g ra te d S ys tems L a b o ra to ry ra wn by I i a N a z emts v | h t: i s cove ry B o a rd . c h o c P a ge of

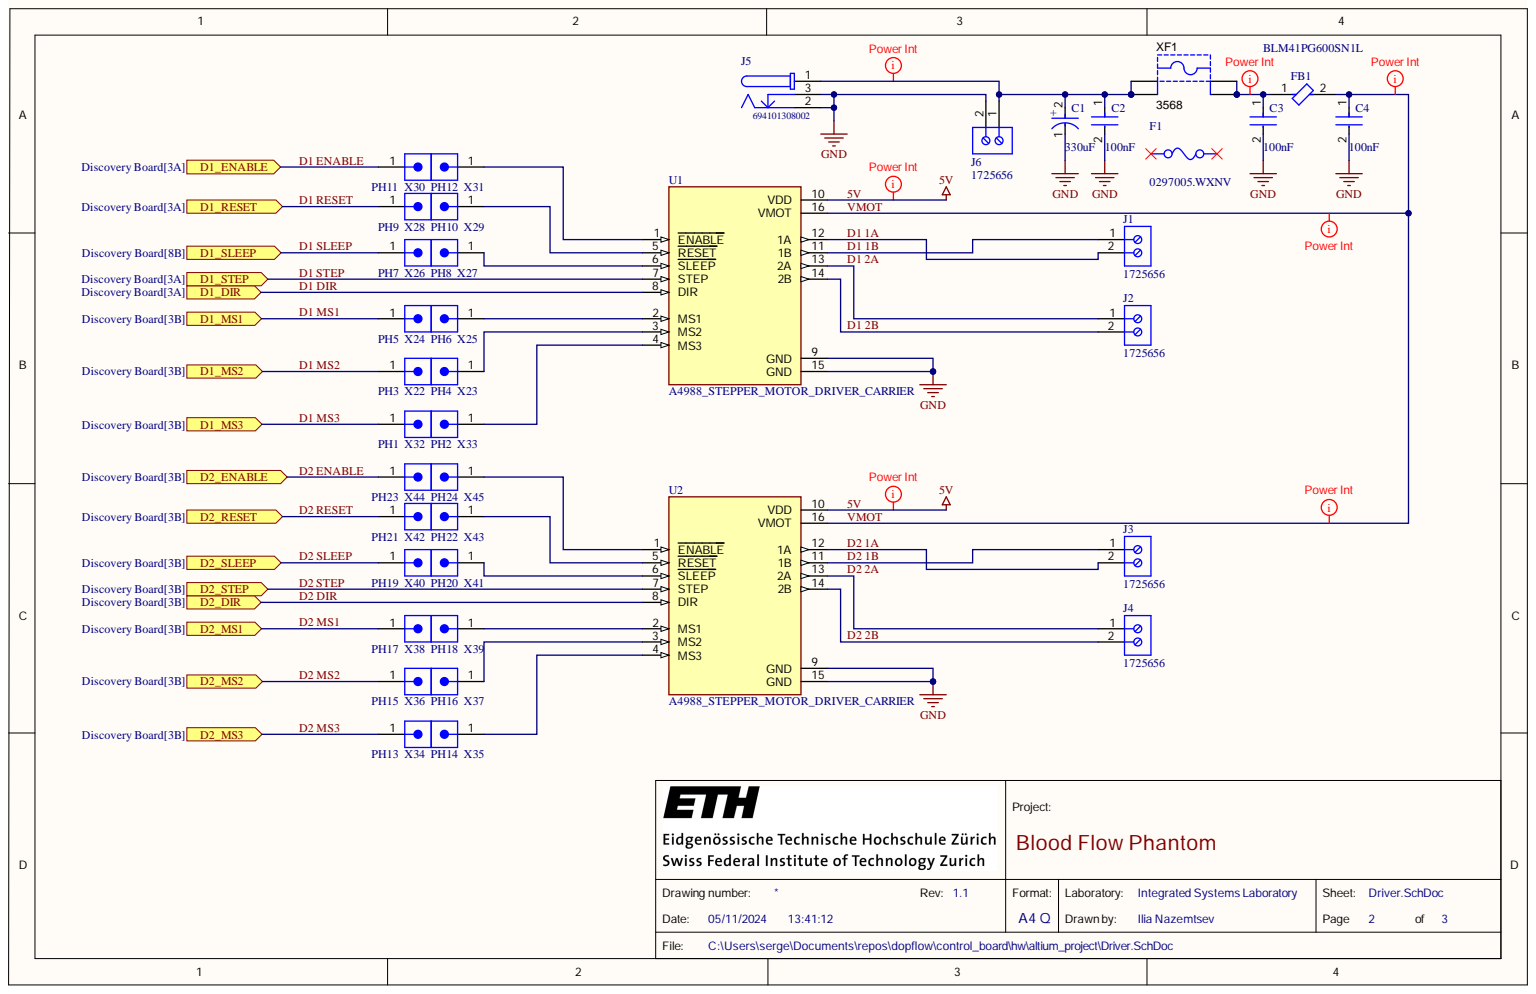
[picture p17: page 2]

5 6 Power I n t

Proje ct: B l o o d F l ow P h a n to m

Drawing numbe r: * R ev: 1. 1 D a te : 13:41 : 1 2 | Forma t: A 4 Q | Laboratory: Integrated Sys tems Labora tory Drawn by : Ilia Nazem tsev | Shee t: Driver. S ch D oc Pag e 2 of 3

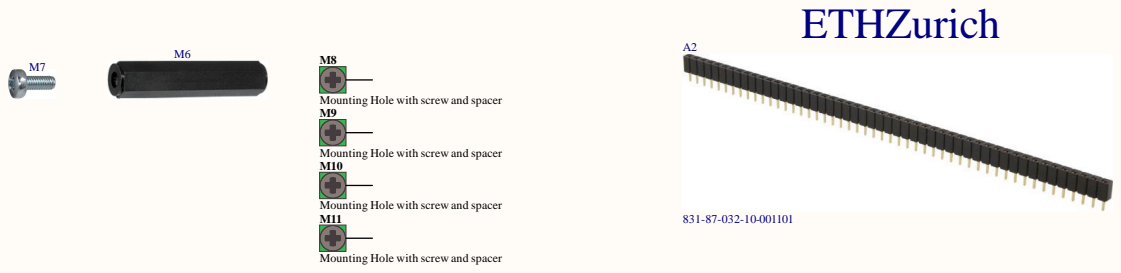
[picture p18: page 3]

Proje ct: B l o o d F l ow P h a n to m

Drawing numbe r: * R ev: 1. 1 D a te : 13:41 : 1 2 | Forma t: A 4 Q | Laboratory: Integrated Sys tems Labora tory Drawn by : Ilia Nazem tsev | Shee t: Mechanical . S ch D oc Pag e 3 of 3

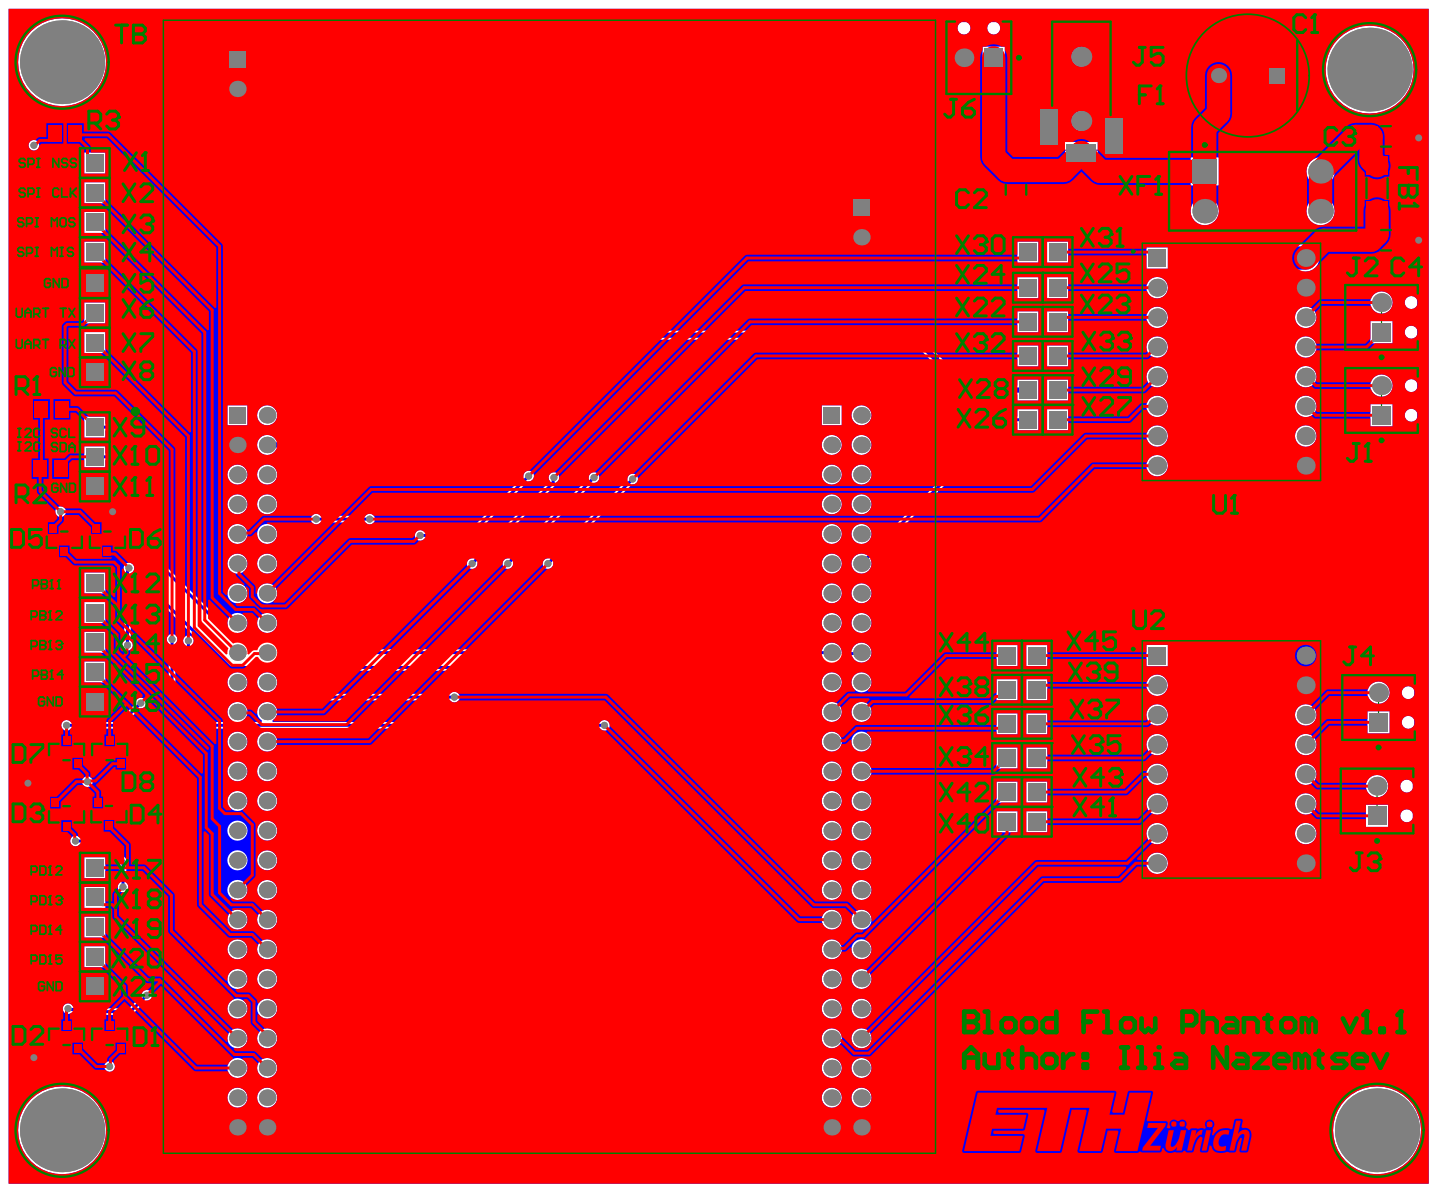
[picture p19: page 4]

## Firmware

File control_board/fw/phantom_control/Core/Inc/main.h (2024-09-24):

/* USER CODE BEGIN Header */
/**
  ******************************************************************************
  * @file           : main.h
  * @brief          : Header for main.c file.
  *                   This file contains the common defines of the application.
  ******************************************************************************
  * @attention
  *
  * Copyright (c) 2023 STMicroelectronics.
  * All rights reserved.
  *
  * This software is licensed under terms that can be found in the LICENSE file
  * in the root directory of this software component.
  * If no LICENSE file comes with this software, it is provided AS-IS.
  *
  ******************************************************************************
  */
/* USER CODE END Header */

/* Define to prevent recursive inclusion -------------------------------------*/
#ifndef __MAIN_H
#define __MAIN_H

#ifdef __cplusplus
extern "C" {
#endif

/* Includes ------------------------------------------------------------------*/
#include "stm32f3xx_hal.h"

/* Private includes ----------------------------------------------------------*/
/* USER CODE BEGIN Includes */

/* USER CODE END Includes */

/* Exported types ------------------------------------------------------------*/
/* USER CODE BEGIN ET */

/* USER CODE END ET */

/* Exported constants --------------------------------------------------------*/
/* USER CODE BEGIN EC */

/* USER CODE END EC */

/* Exported macro ------------------------------------------------------------*/
/* USER CODE BEGIN EM */

/* USER CODE END EM */

void HAL_TIM_MspPostInit(TIM_HandleTypeDef *htim);

/* Exported functions prototypes ---------------------------------------------*/
void Error_Handler(void);

/* USER CODE BEGIN EFP */

/* USER CODE END EFP */

/* Private defines -----------------------------------------------------------*/
#define DRDY_Pin GPIO_PIN_2
#define DRDY_GPIO_Port GPIOE
#define CS_I2C_SPI_Pin GPIO_PIN_3
#define CS_I2C_SPI_GPIO_Port GPIOE
#define MEMS_INT3_Pin GPIO_PIN_4
#define MEMS_INT3_GPIO_Port GPIOE
#define MEMS_INT4_Pin GPIO_PIN_5
#define MEMS_INT4_GPIO_Port GPIOE
#define OSC32_IN_Pin GPIO_PIN_14
#define OSC32_IN_GPIO_Port GPIOC
#define OSC32_OUT_Pin GPIO_PIN_15
#define OSC32_OUT_GPIO_Port GPIOC
#define OSC_IN_Pin GPIO_PIN_0
#define OSC_IN_GPIO_Port GPIOF
#define OSC_OUT_Pin GPIO_PIN_1
#define OSC_OUT_GPIO_Port GPIOF
#define B1_Pin GPIO_PIN_0
#define B1_GPIO_Port GPIOA
#define MOT_DIR_Pin GPIO_PIN_1
#define MOT_DIR_GPIO_Port GPIOA
#define N_MOTOR_EN_Pin GPIO_PIN_3
#define N_MOTOR_EN_GPIO_Port GPIOA
#define SPI1_SCK_Pin GPIO_PIN_5
#define SPI1_SCK_GPIO_Port GPIOA
#define SPI1_MISO_Pin GPIO_PIN_6
#define SPI1_MISO_GPIO_Port GPIOA
#define SPI1_MISOA7_Pin GPIO_PIN_7
#define SPI1_MISOA7_GPIO_Port GPIOA
#define MS1_Pin GPIO_PIN_0
#define MS1_GPIO_Port GPIOB
#define MS2_Pin GPIO_PIN_1
#define MS2_GPIO_Port GPIOB
#define MS3_Pin GPIO_PIN_2
#define MS3_GPIO_Port GPIOB
#define LD4_Pin GPIO_PIN_8
#define LD4_GPIO_Port GPIOE
#define LD3_Pin GPIO_PIN_9
#define LD3_GPIO_Port GPIOE
#define LD5_Pin GPIO_PIN_10
#define LD5_GPIO_Port GPIOE
#define LD7_Pin GPIO_PIN_11
#define LD7_GPIO_Port GPIOE
#define LD9_Pin GPIO_PIN_12
#define LD9_GPIO_Port GPIOE
#define LD10_Pin GPIO_PIN_13
#define LD10_GPIO_Port GPIOE
#define LD8_Pin GPIO_PIN_14
#define LD8_GPIO_Port GPIOE
#define LD6_Pin GPIO_PIN_15
#define LD6_GPIO_Port GPIOE
#define SWITCH1_Pin GPIO_PIN_11
#define SWITCH1_GPIO_Port GPIOB
#define SWITCH2_Pin GPIO_PIN_12
#define SWITCH2_GPIO_Port GPIOB
#define SWDIO_Pin GPIO_PIN_13
#define SWDIO_GPIO_Port GPIOA
#define SWCLK_Pin GPIO_PIN_14
#define SWCLK_GPIO_Port GPIOA
#define SWO_Pin GPIO_PIN_3
#define SWO_GPIO_Port GPIOB
#define I2C1_SCL_Pin GPIO_PIN_6
#define I2C1_SCL_GPIO_Port GPIOB
#define I2C1_SDA_Pin GPIO_PIN_7
#define I2C1_SDA_GPIO_Port GPIOB
#define MEMS_INT1_Pin GPIO_PIN_0
#define MEMS_INT1_GPIO_Port GPIOE
#define MEMS_INT2_Pin GPIO_PIN_1
#define MEMS_INT2_GPIO_Port GPIOE

/* USER CODE BEGIN Private defines */
#define CHANNEL_STEP TIM_CHANNEL_3
/* USER CODE END Private defines */

#ifdef __cplusplus
}
#endif

#endif /* __MAIN_H */

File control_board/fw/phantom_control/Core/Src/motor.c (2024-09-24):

/*
 * Copyright (C) 2024 ETH Zurich. All rights reserved.
 *
 * Authors: Josquin Tille, ETH Zurich
 *
 * Licensed under the Apache License, Version 2.0 (the "License");
 * you may not use this file except in compliance with the License.
 * You may obtain a copy of the License at
 *
 *      http://www.apache.org/licenses/LICENSE-2.0
 *
 * Unless required by applicable law or agreed to in writing, software
 * distributed under the License is distributed on an "AS IS" BASIS,
 * WITHOUT WARRANTIES OR CONDITIONS OF ANY KIND, either express or implied.
 * See the License for the specific language governing permissions and
 * limitations under the License.
 * 
 * SPDX-License-Identifier: Apache-2.0
 */

#include "motor.h"
#include "usbd_cdc_if.h"


#ifdef CMSIS_OS_H_
	#include "cmsis_os.h"

	#define SLEEP(milisec) osDelay(milisec)
#else
	#define SLEEP(milisec) HAL_Delay(milisec)
#endif

#define RPM_PACE_CONVERSION 	300000
#define NOMINAL_MOTOR_PACE 		1500U // [us/m]
#define NOMINAL_ACCELERATION 	50000 // ms*us/step
#define MAX_RPM_STEP 			180
#define MIN_PACE 				100U // [us/m]

#define PACE_DIV(quotien, pace) ((pace)< MIN_PACE?0:(quotien)/(pace))
#define TO_RPM(pace) PACE_DIV(RPM_PACE_CONVERSION, pace)

#define GPIO_SWITCH_FULL 	SWITCH2_GPIO_Port, SWITCH2_Pin
#define GPIO_SWITCH_EMPTY 	SWITCH1_GPIO_Port, SWITCH1_Pin

#define OC_TIMER &htim2

typedef enum
{
	FULL_STEP,
	HALF_STEP,
	QUARTER_STEP,
	EIGHTH_STEP,
	SIXTEENTH_STEP
} MStepType;

extern TIM_HandleTypeDef htim2;
static uint32_t motor_pace = 0;

static void set_micro_step_pin(MStepType m_step_type)
{
	switch(m_step_type)
	{
	case FULL_STEP:
		HAL_GPIO_WritePin(GPIOB, MS1_Pin|MS2_Pin|MS3_Pin, GPIO_PIN_RESET);
		break;
	case HALF_STEP:
		HAL_GPIO_WritePin(GPIOB, MS2_Pin|MS3_Pin, GPIO_PIN_RESET);
		HAL_GPIO_WritePin(GPIOB, MS1_Pin, GPIO_PIN_SET);
		break;
	case QUARTER_STEP:
		HAL_GPIO_WritePin(GPIOB, MS1_Pin|MS3_Pin, GPIO_PIN_RESET);
		HAL_GPIO_WritePin(GPIOB, MS2_Pin, GPIO_PIN_SET);
		break;
	case EIGHTH_STEP:
		HAL_GPIO_WritePin(GPIOB, MS3_Pin, GPIO_PIN_RESET);
		HAL_GPIO_WritePin(GPIOB, MS1_Pin|MS2_Pin, GPIO_PIN_SET);
		break;
	case SIXTEENTH_STEP:
		HAL_GPIO_WritePin(GPIOB, MS1_Pin|MS2_Pin|MS3_Pin, GPIO_PIN_SET);
		break;
	default:
		return;
	}
}

static void set_micro_step_mode(uint32_t* tim_per_step)
{
	const uint16_t min_us_per_step = 1400;
	uint8_t i = 0;
	for(i=0; i<4; ++i)
	{
		if(*tim_per_step < min_us_per_step)
		{
			set_micro_step_pin(FULL_STEP+i);
			return;
		}
		*tim_per_step >>= 1;
	}
	set_micro_step_pin(SIXTEENTH_STEP);

}

/*
 * Function:  motor_set_pace
 * --------------------
 * set the motor pace to
 *
 *  tim_per_step: number of us per step
 *
 *  returns: void
 */
void motor_set_pace(uint32_t tim_per_step)
{
	static uint8_t is_tim_stopped = 0;

	motor_pace = tim_per_step;

	set_micro_step_mode(&tim_per_step);

	if(tim_per_step <= MIN_PACE)
	{	// stop the timer
		HAL_TIM_OC_Stop(OC_TIMER,CHANNEL_STEP);
		// disable motor
		HAL_GPIO_WritePin(MOT_DIR_GPIO_Port,N_MOTOR_EN_Pin, GPIO_PIN_SET);
		is_tim_stopped = 1;
	}
	else
	{
		if(is_tim_stopped)
		{	// restart the timer if it was stopped.
			HAL_TIM_OC_Start(OC_TIMER, CHANNEL_STEP);
			// enable motor
			HAL_GPIO_WritePin(MOT_DIR_GPIO_Port,N_MOTOR_EN_Pin, GPIO_PIN_RESET);
			is_tim_stopped = 0;
		}
		// divide by 2 for the length until toggle
		tim_per_step >>= 1;
		__HAL_TIM_SET_AUTORELOAD(OC_TIMER, tim_per_step-1);
	}
}

uint8_t motor_is_syringe_empty()
{
	return HAL_GPIO_ReadPin(GPIO_SWITCH_EMPTY) == GPIO_PIN_RESET;
}

uint8_t motor_is_syringe_full()
{
	return HAL_GPIO_ReadPin(GPIO_SWITCH_FULL) == GPIO_PIN_RESET;
}

void motor_set_direction(GPIO_PinState dir)
{
	HAL_GPIO_WritePin(MOT_DIR_GPIO_Port, MOT_DIR_Pin, dir);
}


void accelerate_to(uint32_t target_pace, uint16_t acc_step)
{
	// acc_step is in ms * us/step
	const uint16_t sleep_time = 10;
	const uint16_t pace_incr = acc_step/sleep_time;
	// number of step if it starts from a speed of 0
	const uint16_t num_step = PACE_DIV(pace_incr,target_pace);
	const uint16_t base_pace_idx = PACE_DIV(pace_incr,motor_pace)+1;

	uint16_t i = 0;
	//USBD_print("Accelerate %u to %u; %u step \n\r", motor_pace, target_pace, num_step);
	for(i = base_pace_idx; i < num_step ; ++i)
	{
		SLEEP(sleep_time);
		motor_set_pace(pace_incr/i);
	}
	SLEEP(sleep_time);
	motor_set_pace(target_pace);

}

void motor_reverse_at_limit()
{
	if(motor_is_syringe_empty())
		motor_set_direction(BACKWARD_DIR);

	if(motor_is_syringe_full())
		motor_set_direction(FORWARD_DIR);
}

void motor_fill_when_empty()
{
	const uint16_t sleep_time = 10;
	const uint32_t current_pace = motor_pace;

	if(motor_is_syringe_empty())
	{
		USBD_print("Refill in progress...\r\n");
		motor_set_direction(BACKWARD_DIR);
		motor_set_pace(0);
		accelerate_to(NOMINAL_MOTOR_PACE, NOMINAL_ACCELERATION);

		while (!motor_is_syringe_full())
		{
			SLEEP(sleep_time);
		}
		motor_set_direction(FORWARD_DIR);
		// restart
		motor_set_pace(0);
		accelerate_to(current_pace, NOMINAL_ACCELERATION);
		USBD_print("Refill done!\r\n");
	}
}

void calibrate()
{

	const uint16_t sleep_time = 10;
	motor_set_pace(NOMINAL_MOTOR_PACE);

	motor_set_direction(FORWARD_DIR);
	while (!motor_is_syringe_empty())
	{
		SLEEP(sleep_time);
	}

	motor_set_direction(BACKWARD_DIR);
	while (!motor_is_syringe_full())
	{
		SLEEP(sleep_time);
	}

}

void motor_init()
{
	motor_set_pace(0);
	motor_set_direction(FORWARD_DIR);
}

void motor_update_pace_state(uint32_t pace)
{
	// if the acceleration is too high,
	if((int32_t)TO_RPM(pace)-(int32_t)TO_RPM(motor_pace) > MAX_RPM_STEP)
	{
		accelerate_to(pace, NOMINAL_ACCELERATION);
	}
	else
	{
		motor_set_pace(pace);
	}
	USBD_print("Pace set to %u us/steps, %u RPM\n\r", pace, TO_RPM(pace));
}

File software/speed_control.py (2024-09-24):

"""
   Copyright (C) 2024 ETH Zurich. All rights reserved.
   Author: Josquin Tille, ETH Zurich
   
   Licensed under the Apache License, Version 2.0 (the "License");
   you may not use this file except in compliance with the License.
   You may obtain a copy of the License at
       http://www.apache.org/licenses/LICENSE-2.0
   Unless required by applicable law or agreed to in writing, software
   distributed under the License is distributed on an "AS IS" BASIS,
   WITHOUT WARRANTIES OR CONDITIONS OF ANY KIND, either express or implied.
   See the License for the specific language governing permissions and
   limitations under the License.

   SPDX-License-Identifier: Apache-2.0
"""

import tkinter as tk
from tkinter import ttk
from tkinter import filedialog as fd
from matplotlib.figure import Figure
from matplotlib.backends.backend_tkagg import FigureCanvasTkAgg
import serial
import numpy as np
import threading

import time
import serial.tools.list_ports

from heart_rate import PulseWave, HeartRateWave

BAUD_RATE = 115200

def get_ports():
    ports = serial.tools.list_ports.comports()
    port_list = []
    desc_list = []

    for port, desc, hwid in sorted(ports):
        port_list += [port]
        desc_list += [desc]

    return port_list, desc_list

class MyGUI:
    def __init__(self, root):
        self.root = root
        self.root.title("Phantom Controller")

        # COM Port section
        com_frame = ttk.LabelFrame(root, text="COM Port Control")
        com_frame.grid(row=0, column=0, padx=10, pady=10, sticky=tk.W+tk.E+tk.N+tk.S)

        self.port_var = tk.StringVar()
        port_label = ttk.Label(com_frame, text="Select COM Port:")
        port_label.grid(row=0, column=0, padx=5, pady=5, sticky=tk.W)

        self.port_list, port_options = get_ports()
        self.port_combobox = ttk.Combobox(com_frame, textvariable=self.port_var, values=port_options, state="readonly")
        self.port_combobox.grid(row=0, column=1, padx=5, pady=5, sticky=tk.W)

        self.open_button = ttk.Button(com_frame, text="Open COM", command=self.open_com)
        self.open_button.grid(row=1, column=1, columnspan=2, padx=5, pady=5, sticky=tk.W)

        self.is_port_open = False


        # Graph section
        graph_frame = ttk.LabelFrame(root, text="Graph Control")
        graph_frame.grid(row=1, column=0, padx=10, pady=10, sticky=tk.W+tk.E+tk.N+tk.S)

        # Select Manual or pulse
        self.speed_mode_var = tk.StringVar(value="Manual")
        mode_radio1 = ttk.Radiobutton(graph_frame, text="Set manual speed", variable=self.speed_mode_var, value="Manual", command=self.update_all)
        mode_radio1.grid(row=0, column=0, padx=5, pady=5, sticky=tk.W)


        mode_radio2 = ttk.Radiobutton(graph_frame, text="Send blood flow pulses", variable=self.speed_mode_var, value="BFP", command=self.update_all)
        mode_radio2.grid(row=1, column=0, padx=5, pady=5, sticky=tk.W)
        #mode_radio2["state"] = "disabled"
        mode_radio3 = ttk.Radiobutton(graph_frame, text="Custom Pulses", variable=self.speed_mode_var, value="Custom", command=self.update_all)
        mode_radio3.grid(row=0, column=1, padx=5, pady=5, sticky=tk.W)
        self.load_file_button = ttk.Button(graph_frame, text="Load File", command=self.load_pulse_file)
        self.load_file_button.grid(row=1, column=1, padx=5, pady=5, sticky=tk.W)


        # Slider amplitude
        self.MAX_SPEED = 1 # m/s
        slider_frame = ttk.Frame(graph_frame)
        slider_frame.grid(row=2, column=0, rowspan=2, columnspan=4, padx=5, pady=5, sticky=tk.W)

        self.slider_amp_var = tk.DoubleVar(value=0)
        self.slider_amp_var.trace('w', self.update_amplitude)
        slider_amp_label = ttk.Label(slider_frame, text="Amplitude:")
        slider_amp_label.grid(row=0, column=0, padx=5, pady=5, sticky=tk.W)


        self.slider_amp = ttk.Scale(slider_frame, from_=0, to=self.MAX_SPEED, variable=self.slider_amp_var, orient=tk.HORIZONTAL, command=self.update_slider_amp)
        self.slider_amp.grid(row=0, column=1, columnspan=2, padx=5, pady=5, sticky=tk.W)

        slider_amp_entry = ttk.Entry(slider_frame, width=5, textvariable=self.slider_amp_var)
        slider_amp_entry.grid(row=0, column=3, padx=5, pady=5, sticky=tk.W)

        # hr slider
        self.slider_freq_var = tk.DoubleVar(value=60)
        self.slider_freq_var.trace('w', self.update_freq)
        slider_freq_label = ttk.Label(slider_frame, text="Frequency [bpm]:")
        slider_freq_label.grid(row=1, column=0, padx=5, pady=5, sticky=tk.W)

        slider_freq = ttk.Scale(slider_frame, from_=10, to=120, variable=self.slider_freq_var, orient=tk.HORIZONTAL, command=self.update_slider_freq)
        slider_freq.grid(row=1, column=1, columnspan=2, padx=5, pady=5, sticky=tk.W)

        slider_freq_entry = ttk.Entry(slider_frame, width=5, textvariable=self.slider_freq_var)
        slider_freq_entry.grid(row=1, column=3, padx=5, pady=5, sticky=tk.W)

        # Unit
        unit_frame = ttk.Frame(graph_frame)
        unit_frame.grid(row=5, column=0, columnspan=2, padx=5, pady=5, sticky=tk.W)
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

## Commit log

2024-09-24 Initial release
    [BOM.xlsx, Barrel_holder_1.stl, Discovery Board.SchDoc, Driver.SchDoc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]
2024-11-04 Updated BOMs, cleaned READMEs
    [phantom_BOM_new.xlsx, pump_BOM.xlsx]
2024-11-05 Fixed an issue #1 and #4
    [Discovery Board.SchDoc, Driver.SchDoc, Mechanical.SchDoc, PCB.GBL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]
2024-11-05 Updated READMEs and added assembly video
